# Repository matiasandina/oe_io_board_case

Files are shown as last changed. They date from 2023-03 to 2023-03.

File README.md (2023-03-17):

## Intro

This repository contains the files to cut a case for the [Open Ephys Input Output board](https://open-ephys.org/acquisition-system/io-board-pcb).
There are two versions of files, one for the regular IO board, and another for a IO board combined with a db25 terminal block.

* [Open Ephys IO Case](https://github.com/matiasandina/oe_io_board_case#open-ephys-io-case)
* [Open Ephys IO + db25 Case](https://github.com/matiasandina/oe_io_board_case#open-ephys-io--db25-case)

## Open Ephys IO Case

This is a simple project based on 2 layer acrylic that is laser cut using files. The main motivation is to go from this classical cardboard + tape approach:

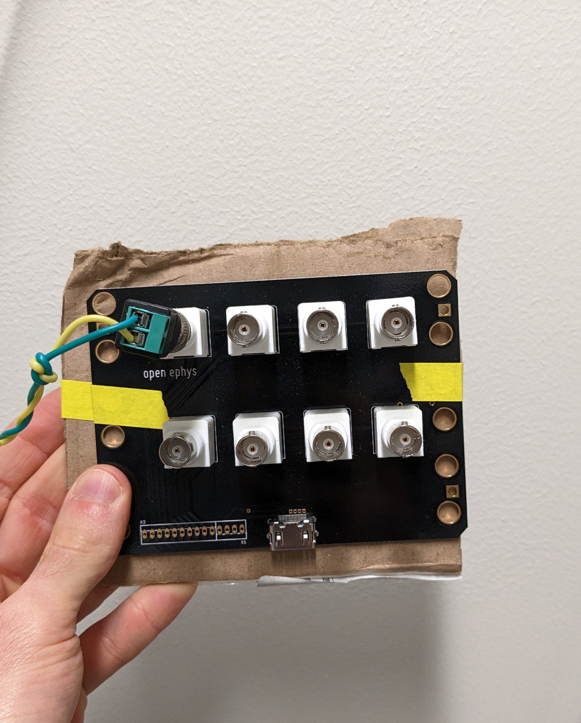
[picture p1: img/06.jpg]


To this slightly better version:

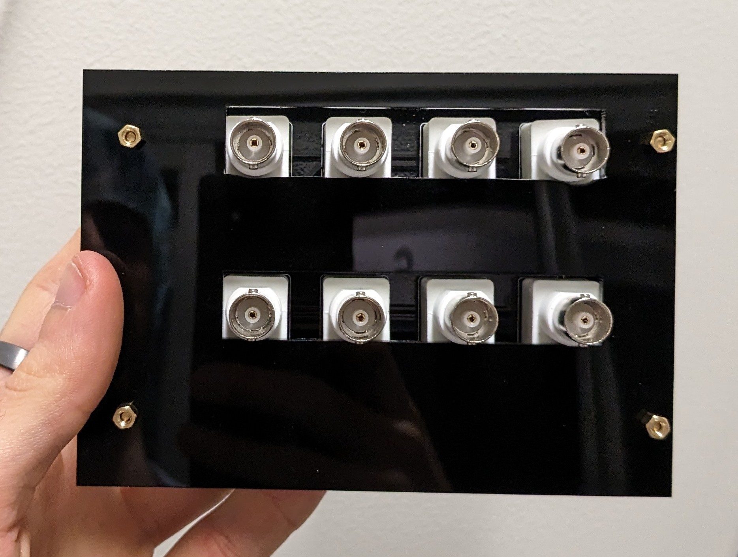
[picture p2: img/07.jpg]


This plays nicely with the Acquisition Board

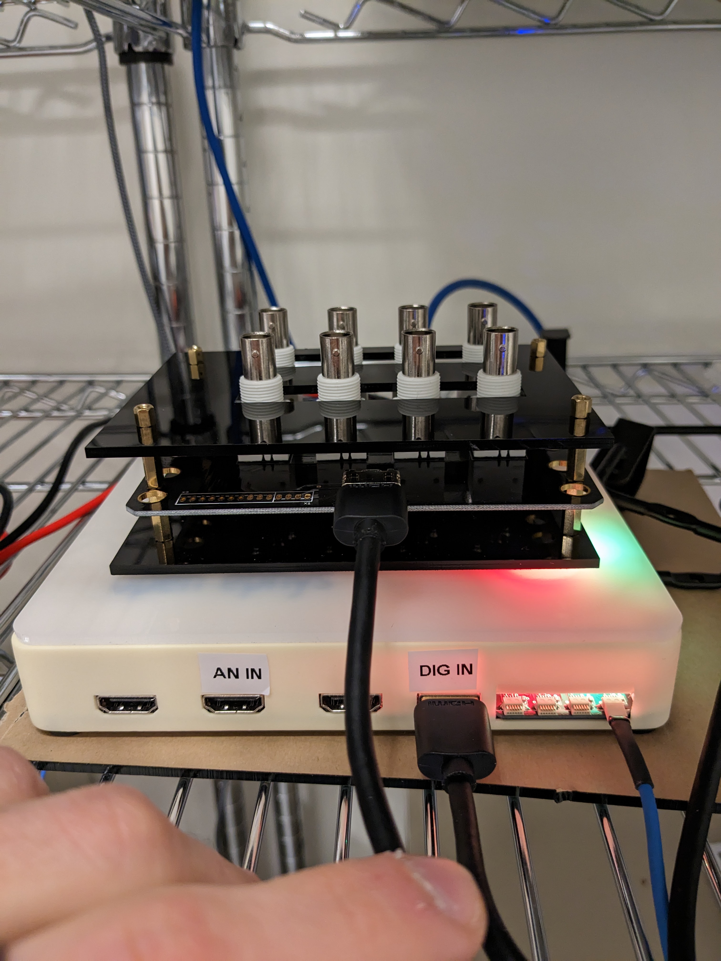
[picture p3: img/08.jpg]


### Materials

* M3 15 or 20 mm bronze standoffs.
* Laser cut case. Files found in this repository.

## Open Ephys IO + db25 Case

This project used a generic db25 terminal block and might need to be adjusted. See [here](https://www.amazon.com/Connector-D-sub-25-pin-Terminal-Breakout/dp/B073RG3GG6/ref=asc_df_B073RG3GG6/?tag=hyprod-20&linkCode=df0&hvadid=216539509836&hvpos=&hvnetw=g&hvrand=17758274187648212718&hvpone=&hvptwo=&hvqmt=&hvdev=c&hvdvcmdl=&hvlocint=&hvlocphy=9002000&hvtargid=pla-348800028947&psc=1) for the link.
We also used a male-female db25 cable (such as [this one](https://www.amazon.com/dp/B092QWDZQZ/ref=twister_B092QTYJWY?_encoding=UTF8&th=1)) to connect the db25 terminal into a TDT RZ10X system.

This provided 8 digital and could be expanded by wiring extra channels to another IO board if needed.
An additional advantage is the use of a single cable (the db25 male-female) instead of multiple BNC cables at the input of the RZ10X, which makes things cleaner.

The pinout for the TDT can be found [here](https://www.tdt.com/docs/hardware/rz10-lux-integrated-processor/#db25-digital-io-pinout) and reproduced below.



### Materials

* generic db25 terminal block. See [here](https://www.amazon.com/Connector-D-sub-25-pin-Terminal-Breakout/dp/B073RG3GG6/ref=asc_df_B073RG3GG6/?tag=hyprod-20&linkCode=df0&hvadid=216539509836&hvpos=&hvnetw=g&hvrand=17758274187648212718&hvpone=&hvptwo=&hvqmt=&hvdev=c&hvdvcmdl=&hvlocint=&hvlocphy=9002000&hvtargid=pla-348800028947&psc=1) for the link. You might need to adjust the files if you use a different terminal, but the process should work because it's just wire!
* Male-female db25 cable such as [this one](https://www.amazon.com/dp/B092QWDZQZ/ref=twister_B092QTYJWY?_encoding=UTF8&th=1)
* M3 20 mm bronze standoffs
* 2 precision screwdrivers for the terminals
* Phoenix style 10 position terminal blocks. We bought 10 instead of 9 because it was easier to get the generic parts from [here](https://www.amazon.com/Augiimor-15PCS-2-54mm-Terminal-Connector/dp/B08B3P8BF3/ref=sr_1_1?content-id=amzn1.sym.ea945d40-8e84-42be-ad5c-249b9bca6a40%3Aamzn1.sym.ea945d40-8e84-42be-ad5c-249b9bca6a40&crid=LO0KLJ0QGMNO&keywords=Terminal+Blocks&pd_rd_r=34f6a4ff-55dc-4279-a9ce-c62dfcd055c4&pd_rd_w=BgHsc&pd_rd_wg=q5rzY&pf_rd_p=ea945d40-8e84-42be-ad5c-249b9bca6a40&pf_rd_r=XCCGPE5VDCCF3R8Z1M9B&pid=rYagDl8&qid=1677857597&refinements=p_n_feature_thirteen_browse-bin%3A18945667011&s=industrial&sprefix=2.54%2Bmm%2Bmount%2Bterminal%2Bblock%2Ctools%2C73&sr=1-1)
* Soldering iron and misc
* 22 AWG wires
* Tape
* Laser cut case. Files found in this repository.

### Assembly

Solder the phoenix-style terminal blocks to the Open Ephys Input Output board. To make things cleaner, we soldered with the exits looking "inward". Later on, add standoffs to the acrylic base layer

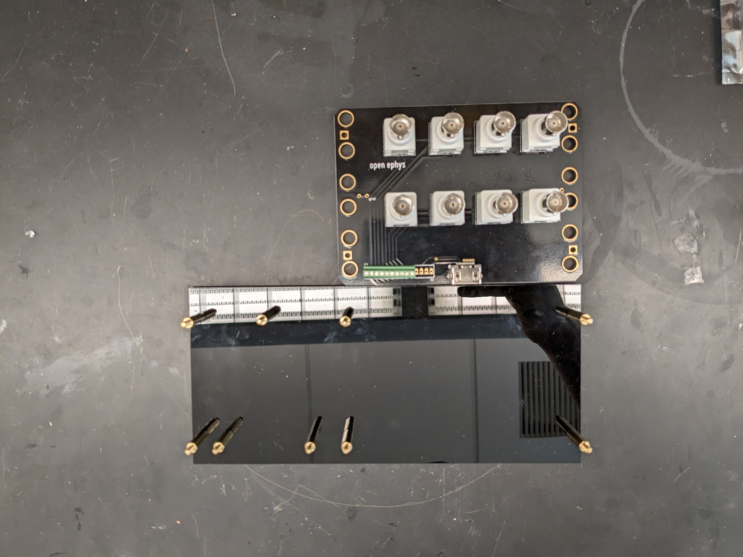
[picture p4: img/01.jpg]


Position the boards and follow the channel map according to the pinout that you want to use. You can use some tape to make things tidier.

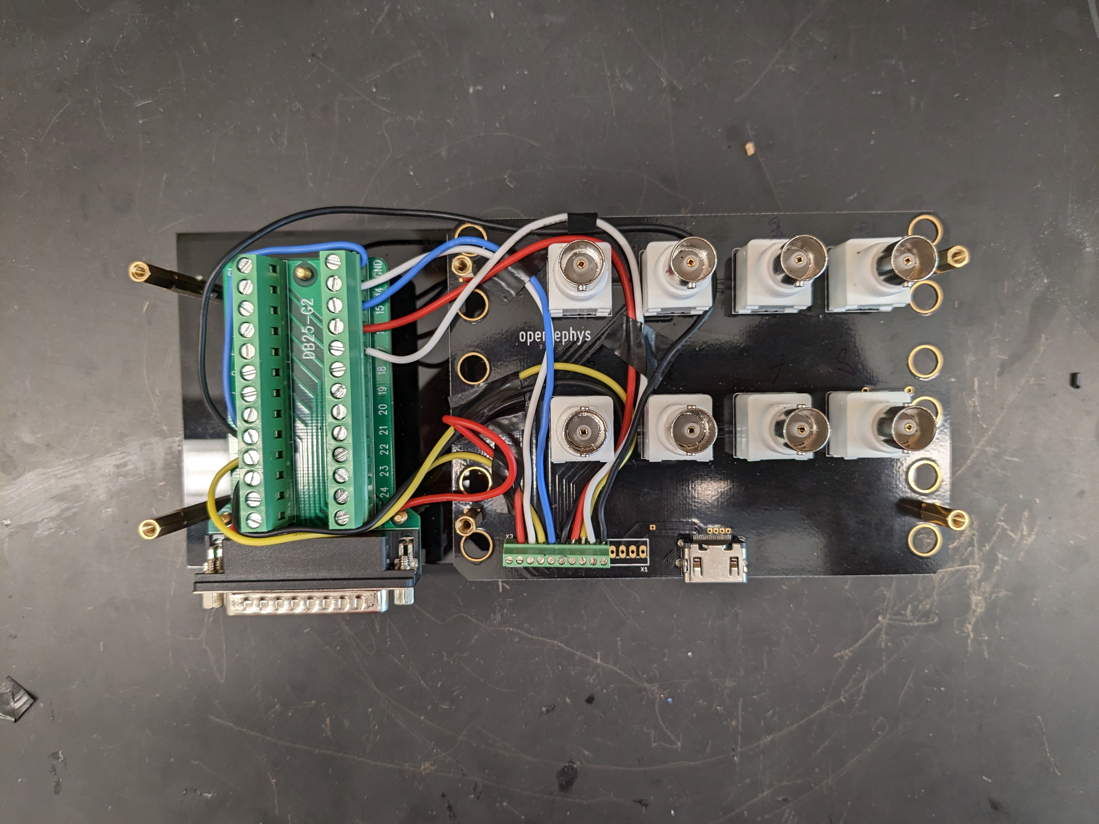
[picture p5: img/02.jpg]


Position the standoffs for the second layer and put the acrylic top. You might need to wiggle things if the fit is too tight.

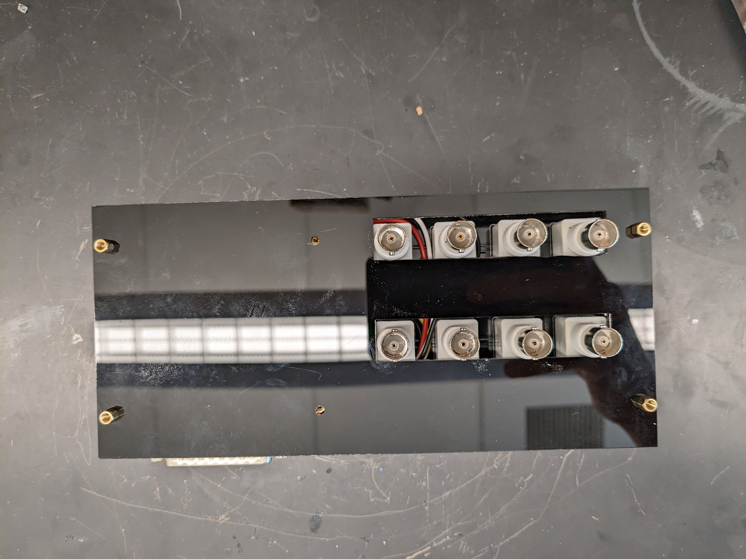
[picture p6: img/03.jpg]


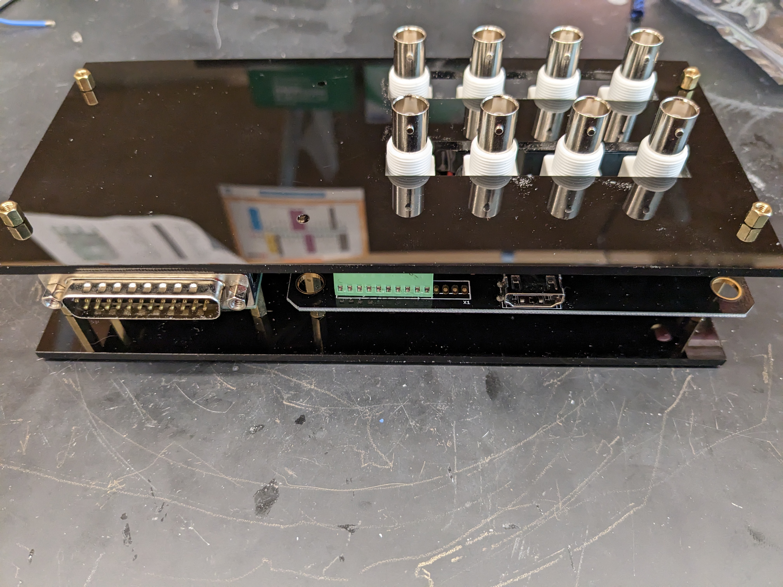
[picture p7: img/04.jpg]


Test the device is working by connecting to your db25 source. In our case, this was a TDT RZ10X, which has a minimal current when idle.



This is a minimal test, you should test that channels are independent by sending pulses in/out of your devices!

## Contribute

This is release of open hardware is 'as is'. If you improve it or build upon it, please file issues or PR to contribute to the community.

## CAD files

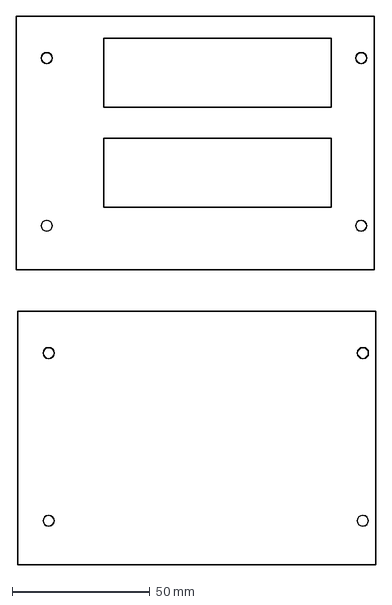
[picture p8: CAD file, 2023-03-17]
v1/oe_io_board_v1.dxf
130.6 x 199.1 mm

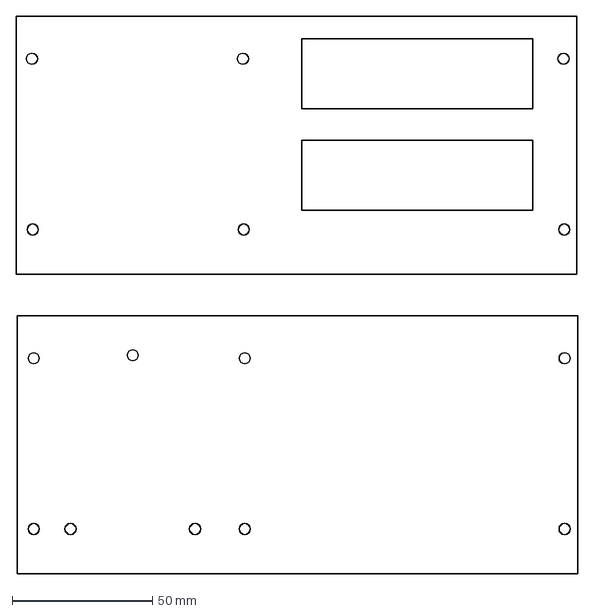
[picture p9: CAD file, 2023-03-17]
v1/oe_io_board_db25_v1.dxf
200.4 x 198.9 mm

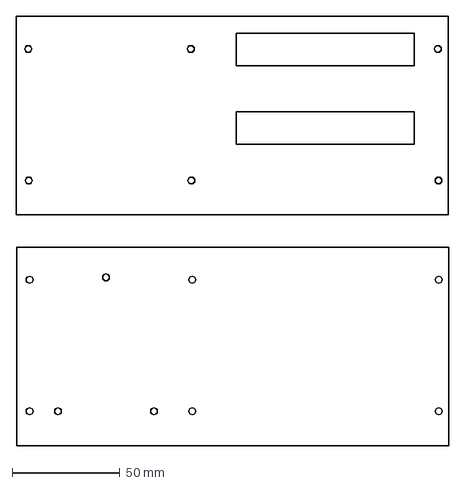
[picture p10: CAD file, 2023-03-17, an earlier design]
v0/dxf/io_board_db25_MLA.dxf
200.4 x 198.9 mm

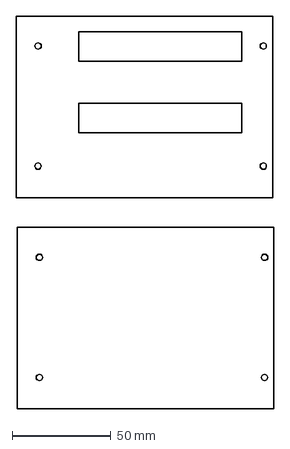
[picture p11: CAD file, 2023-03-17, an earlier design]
v0/dxf/io_board_MLA.dxf
130.6 x 199.1 mm

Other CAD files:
v0/io_board_case.step
v1/io_board_case.f3d
